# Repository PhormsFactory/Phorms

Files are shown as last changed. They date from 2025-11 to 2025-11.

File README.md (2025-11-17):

# Phorms
Open-source 3D printable modules for pharmaceutical applications.

##  📖 Description
Phorms project aims to provide open-source 3D printable modules for pharmaceutical or fine chemistry applications.
Converting batch processes to continuous processes or directly adapting new processes to continuous is widely supported by all regulation agencies worldwide, however investing in such expensive equipments can be a limitation for smaller laboratories.
For now, Phorms' modules are prototypes to support laboratories for quick-testing continuous processes concepts with limited costs and community-driven.
All modules can be connected to each other to build multi-steps processes.

For now, Phorms focuses on unit of operations for producing small molecules such as :
- Small tank modules for reactants and solvents
- Continuous reaction modules
- Continuous liquid/liquid extraction modules
- Continuous crystallization modules
- Continuous cyclonic separators

Avoiding non-3D-printable equipments like pumps, filtration media or valves is important for better accessibility and to limit any extra investments.
For instance, compressed gases like air or nitrogen can be used as driving force for all fluids in the process.
All modules are designed to be as analogic as possible and do not require the user to use any electronic systems for flow regulation or any other purposes.

Each module has an associated documentation which gives printing tips and setups.

## 🛠️ Choice of printing material

Ideally the selected polymer must :
- Resist to acids and bases
- Resist to solvents (organic and aqueous)
- Resist to heat
- Resist to pressure
- Be 3D-printable, preferably FDM
- Not be too expensive

PTFE is the best candidate regarding these constraints, unfortunately it cannot be 3D-printed.
The next one is PVDF, but it required very high printing temperatures that are not supported by many 3D printers. 
Also, it can potentially produce fluor-based gases which could be harmful for inexperienced users.

The most widely used polymers for FDM printing are PLA, ABS or Nylon.
They are not suitable for such applications because of their low melting point and solvent resistance.

In the end, the list could be reduced to 3 candidates : PETG, Polypropylene (PP), and Polycarbonate (PC).
Polypropylene is the polymer used for all the prototypes developed here, it can be hard to print (warping) but manageable with dedicated solutions.
Polypropylene has many advantages like good elasticity and transparency, which could be helpful for some modules.
PETG is easier to print but shows a high hardness and tends to break.
PC is also harder than Polypropylene and very difficult to print, however among those 3 polymers, it has the best resistance to all criteria listed above.

## 🖨️ Printing setup

- Printer : Prusa MK3
- Enclosure : None
- Nozzle : E3D V6 Nozzle X
- Printing sheet : Prusa PP steel sheet (mandatory to avoid warping)
- Slicer : PrusaSlicer
- Filament : FormFutura Centaur PP Natural ⌀1.75mm

While printing, Polypropylene behaves like Nylon and tends to jam the extruder.
It is advised to loosen the extruder as much as possible to avoid any issue.
The detailed printing parameters are specified for each module separately.

## 📁 Files
For each module, the following documents are provided :
- STL file
- STEP file
- FCStd file
- Instructions
- PNG renders

All 3D models are developed with FreeCAD 1.0.0, it is recommended to use ThreadProfile addon for designing fasteners.

## ✅ Available modules (Nov. 2025)
### 🧪 Plug-flow reactor
A plug-flow reactor with integrated heat exchanger without supports.

Status : 🔴 prototype under development

### 📦 Plug-flow reactor kit
A plug-flow reactor linked with 2 tanks, printable in one block without support.
Each tank flow can be regulated with a 'pinch-valve', the heat exchanger goes through all parts of the kit.

Status : 🔴 prototype under development

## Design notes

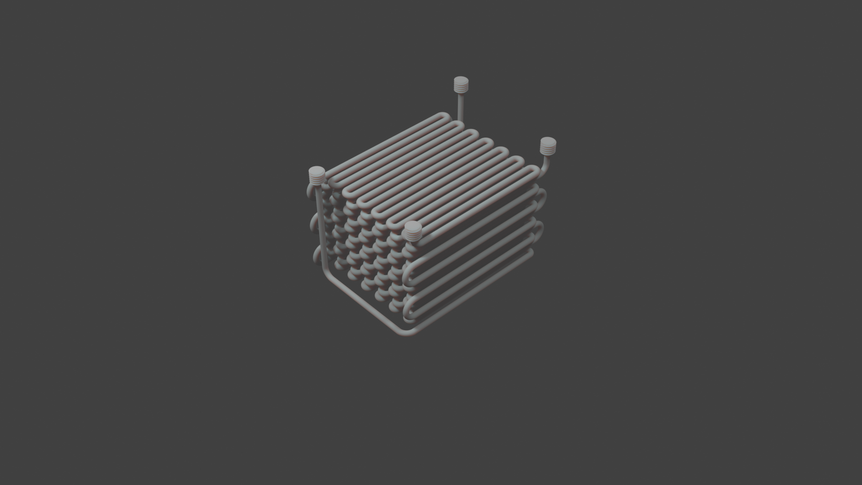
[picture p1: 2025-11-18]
hardware/plug-flow_reactor/docs/pfr_interior.png

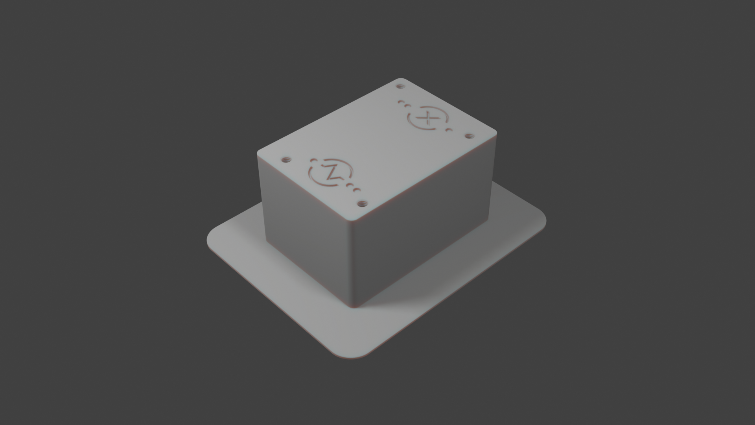
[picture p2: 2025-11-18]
hardware/plug-flow_reactor/docs/pfr_render.png

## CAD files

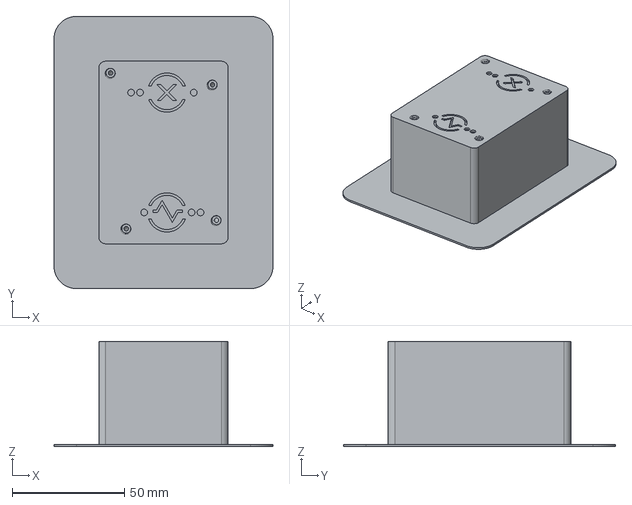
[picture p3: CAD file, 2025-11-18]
hardware/plug-flow_reactor/plug-flow_reactor.step
97.8 x 121.5 x 47.0 mm

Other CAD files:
hardware/plug-flow_reactor/plug-flow_reactor.FCStd

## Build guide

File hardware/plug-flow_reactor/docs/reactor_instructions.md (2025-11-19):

# 🧪 Plug-flow reactor instructions

Renders of the exterior and the internal structure are available below :

[pfr_exterior.png](https://github.com/PhormsFactory/Phorms/blob/main/hardware/plug-flow_reactor/docs/pfr_render.png)

[pfr_interior.png](https://github.com/PhormsFactory/Phorms/blob/main/hardware/plug-flow_reactor/docs/pfr_interior.png)

## 📖 Description

The proposed plug-flow reactor integrates a simple S-shaped design, see the associated PNG images.
It has few parameters to consider :
- Number of channels (straight pipes per layer) : $N$
- Length of each channels : $L$
- Number of layers : $M$
- Pipe diameter : $D$
- Overall spacing between layers and channels : $S$

There are 2 layouts : reactor and heat exchanger.
Each layer $M$ has $N$ channels, all the channels per layer are connected in a linear way via 'U-turns'. 

The heat exchanger starts from the bottom layer $1$ and skips all even numbers of layers.
The top layer $L$ must be also a layer of heat exchanger, meaning that the number of layers $L$ is always an uneven number.
This way the reactor layers are always surrounded by layers of heat exchanger for better heat transfer and is represented by all even number of layers.

It is optimal to operate a continuous heat transfer with two countercurrent fluids compared with co-current fluids. Consequently, the reactor fluid enters at layer $L-1$ and exits at layer $2$ while the heat exchanger fluid enters at layer $1$ and exits at layer $L$. One could use each streams differently, the proposed layout is in accordance with good engineering practices.

Additionally, the layers are arranged in quincunx pattern, which increases the heat transfer performance and reduces the overall height of the model.

The pipe diameter $D$ and overall spacing $S$ parameters can be adjusted but cannot be too small for printing accuracy reasons.

## 🔌 Flow connectors

The reactor has 4 connectors, the symbols on top of the reactor allow to identify the correct connectors :
- Reactor inlet : &#9679;<b>(X)</b>
- Reactor outlet : <b>(X)</b>&#9679;&#9679;
- Heat exchange inlet : &#9679;<b>(Z)</b>
- Heat exchange outlet : <b>(Z)</b>&#9679;&#9679;

The connectors are based on standard M5 BSP OD threads and are 4mm deep.
For instance, one could use pneumatic PL4-M5 fittings for fluid transfer.

## 🖨️ Printing parameters

## ✏️ CAD files
The user can adjust the following variables in the model ('Varset' in FreeCAD) :

| Variable name | Symbol | Minimum recommended value |
| ------------- | ------ | ------------------------- |
| Number of channels | $N$ | 8 |
| Channel length | $L$ | 50.0 mm |
| Number of layers | $M$ | 5 |
| Reactor diameter | $D_1$ | 1.0 mm |
| Heat exchanger diameter | $D_2$ | 1.0 mm |
| Spacing | $S$ | 3.0 mm |

Reactor and heat exchanger volumes are estimated in a dedicated spreadsheet in the CAD file. The average residence time $\tau$ can be estimated knowing the global flowrate $\dot{V}$ as : $\tau = \frac{V}{\dot{V}}$.

## 🧩 STL Download (GitHub Releases)

The model contains a lot of vertices and is heavy. It is available for download on GitHub Releases, link below :

| Link | Version | Size | Status |
| ---- | ------- | ---- | ------ |
| [plug-flow_reactor.stl](https://github.com/PhormsFactory/Phorms/releases/download/v0.1.0-alpha/plug-flow_reactor.stl) | 0.1.0-alpha | 138Mb | Print OK, watertightness tests ongoing |

### Notes
Feedback from early prints to avoid leaks :
- Avoid low nozzle temperatures : 
    - Poor layer adhesion will lead to leaking units and poor pressure resistance
    - Natural finishes become less transparent and interior less visible
- Infill : print with 100% infill to improve structural resistance
- Apply teflon tape on fitting threads
- Avoid low spacing between channels and layers
- Print without pause

### Happy downloading ☀️ ! 
### Contributions and suggestions are always welcome 💬🤝.

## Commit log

2025-11-17 Create LICENCE
    CERN-OHL-S current version (v2) for open-source hardware
2025-11-18 Reactor module files and docs added
    [plug-flow_reactor.FCStd, plug-flow_reactor.step]
